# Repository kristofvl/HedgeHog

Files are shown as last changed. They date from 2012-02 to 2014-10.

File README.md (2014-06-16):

More information about this package can currently be found at:
 http://kristofvl.github.io/HedgeHog/ 

****************************************************************

In short, this repository contains three packages:

1. The HedgeHog firmware (operating system), requires:
    - MPLAB X (free IDE, download from Microchip.com)
    - Microchip Application Library (free library set, download 
      from Microchip.com)

2. The HedgeHog Graphical interface software, requires:
    - the basic python libraries
    - matplotlib

3. The hardware design files for the HedgeHog sensor, requires:
    - eagleCAD (free PCB design tool, download from 
      CadSoftusa.com)

****************************************************************

# User Manual

This manual will help you use your HedgeHog properly. Therefore, we will discuss the following themes

[1) Prepare your computer](#prepare-your-computer)<br>
[2) Configure the HedgeHog](#configure-the-hedgehog)<br>
[3) Start logging](#start-logging)<br>
[4) Download the logged data](#download-the-logged-data)<br>
[5) Display the downloaded data](#display-the-downloaded-data)<br>

## Prepare your computer

There is some software required on your computer in order for the graphical interface to work

* the basic python libraries (https://www.python.org/)
* matplotlib (http://matplotlib.org/)

Once this software is installed, please clone this repository by executing the command

	$ git clone https://github.com/kristofvl/HedgeHog

Now execute the installation script

	$ ./HedgeHog/HHG/install_HHG.py

This will create a few Desktop shortcuts to scripts, that will be discussed later on. Now your computer is set up for working with the HedgeHog.

## Configure the HedgeHog

If you plug in the HedgeHog into the USB-Connector of your PC, it should be recognized correctly now. The install command has created a shortcut to the configuration script. Start the script and choose the desired configuration, then click *Save Settings*. The HedgeHog will unmount, apply the settings and then mount again by itself. Do not unplug it during this process! 
In the configuration script you also have the option of formating your SD-Card. By pressing format the HedgeHog will unmount, format the SD-Card and then remount again.
An other way of formatting your HedgeHog is by using the dd command. In this example, the HedgeHog is mounted at /dev/sdb.

	- cd ~/HedgeHog/HHG/
	- dd if=dd_img/dd.img of=/dev/sdb; sync

Don't forget to configure the HedgeHog after formatting.

In case you dont want to start the configuration script using the created buttons, you can also run them in a terminal. The script is in the folder *~/HedgeHog/HHG/* and is named *conf_HHG.py*. To run it, go to the folder and execute

	- python conf_HHG.py /media/<username>/HedgeHog<HHG-device_id>/config.URE

## Start logging

Now that your HedgeHog has the right configuration, you are ready to start logging. Use the start script, that was also created during the installation. You will find the shortcut on your Desktop. Choose the logging period. The default is set to one week. After pressing start, the HedgeHog will disconnect automatically and start logging. Remember to unplug it form the USB-Connector instantaneously after starting it.

Since firmware version 1.4000, the HedgeHog will continue logging as long as it has energy supply, even if it is plugged into the USB-Connector. When plugged in, the HedgeHog will interrupt the logging process and resume, as soon as it is plugged out. You can visualize the data, as shown in [4) Download the logged data](#download-the-logged-data) and [5) Display the downloaded data](#display-the-downloaded-data) when the device is attatched to your PC.

In case you dont want to start the script using the created buttons, you can also run them in a terminal. The script is in the folder *~/HedgeHog/HHG/* and is named *start_HHG.py*. To run it, go to the folder and execute

	- python start_HHG.py /media/<username>/HedgeHog<HHG-device_id>/config.URE

## Download the logged data

To download the logged data, you can use the download script. A shortcut to the script was also created during the installation. The data will be saved at 

	- ~/hhg_logs/<HHG_device_id>/<date>/d.npz 

where 'HHG-device_id' is the number you entered in the configuration interface and 'date' is the starting date.

## Display the downloaded data

To visualize the data, use the python script in the repository as follows:

	- cd ~/HedgeHog/HHG/
	- ./viz_HHG.py ~/hhg_logs/<HHG_device_id>/<date>/d.npz 

where 'HHG-device_id' is the number you entered in the configuration interface and 'date' is the starting date.

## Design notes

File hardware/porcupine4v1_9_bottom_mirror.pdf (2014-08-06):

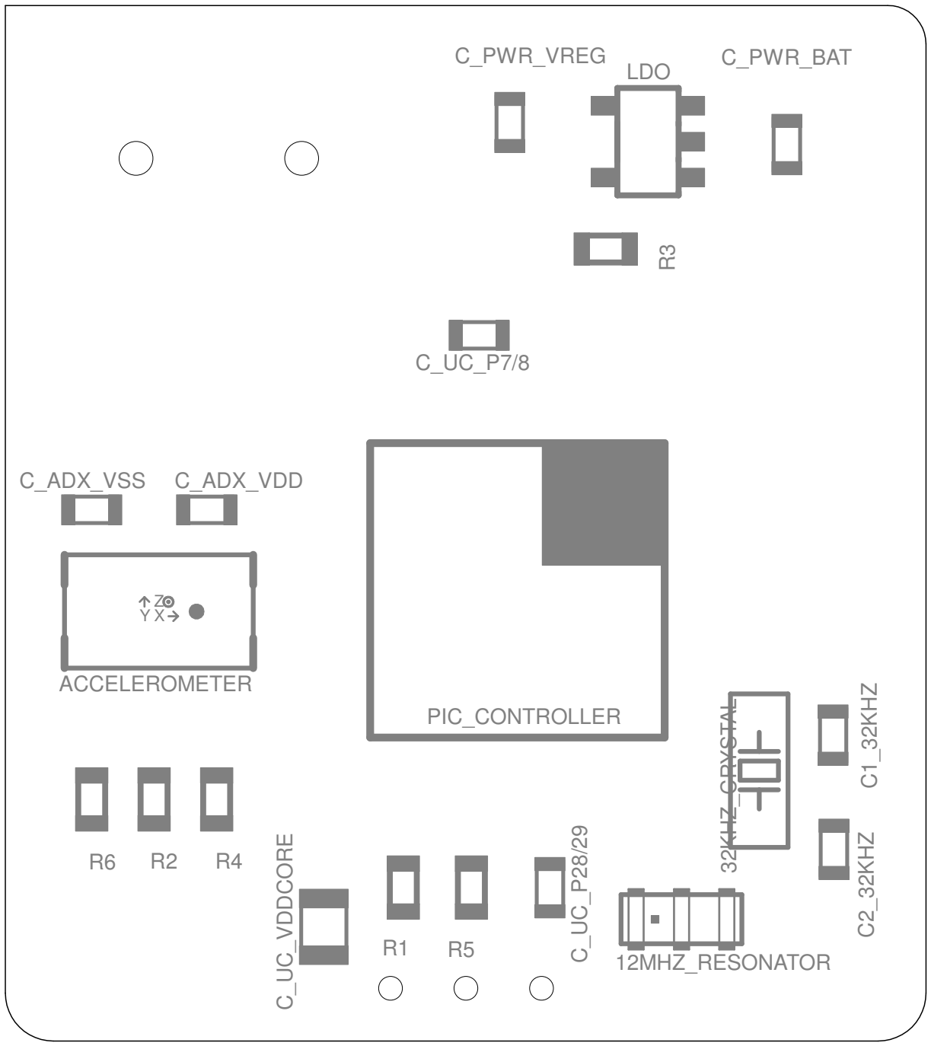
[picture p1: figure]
12MHZ_RESONATOR ³²KHZ_CRYSTAL; C_PWR_BAT; ACCELEROMETER; C_ADX_VSS; C_ADX_VDD; C_PWR_VREG; PIC_CONTROLLER; C2_32KHZ C1_32KHZ; C_UC_VDDCORE; LDO

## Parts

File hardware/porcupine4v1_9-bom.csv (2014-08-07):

BILL OF MATERIAL FROM TEST_WIDERSTAENDE_AUS_RCL.SCH, 29 PARTS, GROUPED BY VALUES, AS OF 05.10.2010 16:00:00
Part | Value | Device | Package | Description | Description2 | Qty | Place_YES/NO | Povided_by_customer_YES/NO | Distributor | Ordernumber | Weblink | Remarks_customer | Unit_price | Total_price | REMARKS_BETA | OPTION1 | OPTION2 | OPTION3
12MHZ_RESONATOR | RESONATORPRQC-C | RESONATORPRQC-C | PRQC-C |  |  | 1 | YES | NO | DigiKey | 478-6318-1-ND | http://www.digikey.de/product-detail/de/PRQC12.00CR5010X000/478-6318-1-ND/2506334 |  | 0.389
32KHZ_CRYSTAL | SMD_CRYSTAL | SMD_CRYSTAL | SMD_CRYSTAL |  |  | 1 | YES | NO | Farnell | 2101349 | de.farnell.com/2101349 |  | 0.801
ACCELEROMETER | ADXL345 | ADXL345 | LGA14 |  |  | 1 | YES | NO | Farnell | 1853935 | de.farnell.com/1853935 |  | 4.15
BAT | 53048-02 | 53048-02 | 53048-02 | CONNECTOR |  | 1 | YES | NO | Farnell | 1012259 | de.farnell.com/1012259 |  | 0.298
C1_32KHZ, C2_32KHZ | 22p | C-EUC0603K | C0603K | CAPACITOR, European symbol |  | 2 | YES | NO | Farnell | 1759057 | de.farnell.com/1759057 |  | 0.009
CHARGER | MAX1551 | MAX1551 | SOT23-5L | Dual-Input USB/AC Adapter 1-Cell Li+ Battery Chargers |  | 1 | YES | NO | Farnell | 1628221 | de.farnell.com/1628221 |  | 1.69
C_ADX_VDD, C_UC_P37 | 0.1u | C-EUC0603K | C0603K | CAPACITOR, European symbol |  | 2 | YES | NO | Farnell | 1759016 | de.farnell.com/1759016 |  | 0.007
C_ADX_VSS, C_PWR_VREG, C_PWR_VUSB | 1u | C-EUC0603K | C0603K | CAPACITOR, European symbol |  | 3 | YES | NO | Farnell | 1759399 | de.farnell.com/1759399 |  | 0.009
C_PWR_BAT | 4.7u | C-EUC0603K | C0603K | CAPACITOR, European symbol |  | 1 | YES | NO | Farnell | 2362098 | de.farnell.com/2362098 |  | 0.053
C_UC_P7/8, C_UC_P28/29 | 0.22u | C-EUC0603K | C0603K | CAPACITOR, European symbol |  | 2 | YES | NO | Farnell | 1759403 | de.farnell.com/1759403 |  | 0.021
C_UC_VDDCORE | 10u | C-EUC0805K | C0805K | CAPACITOR, European symbol | Capacitor, 0805, 10uF, 16V | 1 | YES | NO | Farnell | 1759136 | de.farnell.com/1759136 |  | 0.046
LDO | MCP1824 | MCP1824 | SOT-23-5 | MCP1824T-3302E/OT |  | 1 | YES | NO | Farnell | 1578387 | de.farnell.com/1578387 |  | 0.322
LIGHTSENSE | TSL250 | TSL250 | TSL |  |  | 1 | NO | NO
PIC_CONTROLLER | PIC_P2V6 | PIC_P2V6 | QFN44ML8X8 |  |  | 1 | YES | NO | Farnell | 1706311 | de.farnell.com/1706311 | 10 in EU / 67 in GB | 2.72
R1, R2, R3, R4, R5, R6 | 10k | R-EU_R0603 | R0603 | RESISTOR, European symbol | RESISTOR, 0.1W, 1% | 6 | YES | NO | Farnell | 1469749 | de.farnell.com/1469749 |  | 0.018
SDCARD_CON | MICROSD_CONN | MICROSD_CONN | 460DA40013 |  |  | 1 | YES | NO | Farnell | 1686452 | de.farnell.com/1686452 |  | 1.83
USB_CON | USBCON | USBCON | 248601 | MINI USB 2.0 Connector TypeB |  | 1 | YES | NO | Farnell | 2112367 | de.farnell.com/2112367 |  | 0.41
X1 | PROGCON | PROGCON | 53047-05-OCT | Programmer Connector |  | 1 | NO | NO

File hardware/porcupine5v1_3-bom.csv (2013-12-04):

Part | Value | Device | Package | Description | Description2 | Qty | Place_YES/NO | Povided_by_customer_YES/NO | Distributor | Ordernumber | Weblink | Remarks_customer | Unit_price | Total_price | REMARKS_BETA | OPTION1 | OPTION2 | OPTION3
ACCERELOMETER | ADXL345 | ADXL345 | LGA14 |  |  | 1 | YES | NO | Farnell | 1853935 | de.farnell.com/1853935
BAT | 53048-02 | 53048-02 | 53048-02 | CONNECTOR |  | 1 | YES | NO | Farnell | 1012259 | de.farnell.com/1012259
C1_32KHZ, C2_32KHZ | 22p | C-EUC0603K | C0603K | CAPACITOR, European symbol |  | 2 | YES | NO | Farnell | 1759057 | de.farnell.com/1759057
CHARGER | MAX1551 | MAX1551 | SOT23-5L | Dual-Input USB/AC Adapter 1-Cell Li+ Battery Chargers |  | 1 | YES | NO | Farnell | 1628221 | de.farnell.com/1628221
CON_OLED | OLED_DENSITRON | OLED_DENSITRON | CON_DD-12864WE-1A |  |  | 1 | NO | NO | Farnell | 1829709 | de.farnell.com/1829709
C_ADX_VDD, C_UC_P37 | 0.1u | C-EUC0603K | C0603K | CAPACITOR, European symbol |  | 2 | YES | NO | Farnell | 1759016 | de.farnell.com/1759016
C_ADX_VSS, C_OL_VBREF, C_OL_VDD2, C_PWR_BAT, C_PWR_VREG, C_PWR_VUSB | 1u | C-EUC0603K | C0603K | CAPACITOR, European symbol |  | 6 | YES | NO | Farnell | 1759407 | de.farnell.com/1759407
C_OL_APP_VDD | 10u low ESR | CPOL-EUA/3216-18R | A/3216-18R | POLARIZED CAPACITOR, European symbol |  | 1 | YES | NO | Farnell | 1432318 | de.farnell.com/1432318 | CHECK ESR
C_OL_FB | 1n | C-EUC0603K | C0603K | CAPACITOR, European symbol | Kondensator, 1nF, 50V, 0603, SMD | 1 | YES | NO | Farnell | 722170 | de.farnell.com/722170
C_OL_VCOMH | 4.7u | C-EUC0603K | C0603K | CAPACITOR, European symbol |  | 1 | YES | NO | Farnell | 1833803 | de.farnell.com/1833803
C_OL_VPP | 6.8u low ESR | CPOL-EUA/3216-18R | A/3216-18R | POLARIZED CAPACITOR, European symbol |  | 1 | YES | NO | Farnell | 1457431 | de.farnell.com/1457431 | CHECK ESR
C_PWR_SW, C_UC_VDDCORE | 10u | C-EUC0805K | C0805K | CAPACITOR, European symbol | Capacitor, 0805, 10uF, 16V | 2 | YES | NO | Farnell | 1288204 | de.farnell.com/1288204
C_UC_P7/8, C_UC_P28/29 | 0.22u | C-EUC0603K | C0603K | CAPACITOR, European symbol |  | 2 | YES | NO | Farnell | 1759403 | de.farnell.com/1759403
DIOD_OL | MBR0520 | MBR0520 | SOD123 |  |  | 1 | YES | NO | Farnell | 1467521 | de.farnell.com/1467521
LDO | MCP1824 | MCP1824 | SOT-23-5 | MCP1824T-3302E/OT |  | 1 | YES | NO | Farnell | 1578387 | de.farnell.com/1578387
LIGHTSENSE | TSL250 | TSL250 | TSL |  |  | 1 | NO | NO | Farnell | 1182346 | de.farnell.com/1182346
L_OL | 10uH | LQH3NP | 1212_FOR_INDUCTANCE |  |  | 1 | YES | NO | Farnell | 2219251 | de.farnell.com/2219251
N_MOS_OL |  | MGSF1N02LT1 | SOT-23 | MOS FET |  | 1 | YES | NO | Farnell | 9845372 | de.farnell.com/9845372
PIC_CONTROLLER | PIC_P2V6 | PIC_P2V6 | QFN44ML8X8 |  |  | 1 | YES | NO | Farnell | 1706311 | de.farnell.com/1706311
R1, R2, R3, R4, R5, R6, R7 | 10k | R-EU_R0603 | R0603 | RESISTOR, European symbol | RESISTOR, 0.1W, 1% | 7 | YES | NO | Farnell | 1469748 | de.farnell.com/1469748
R8 | 0.12 1% 0.5W | RESISTOR_PAN_ERJB3CFR12V | 0805_UPSIDEDOWN |  |  | 1 | YES | NO | Farnell | 1750969 | de.farnell.com/1750969
R9 | 110k 1% 0.125W | R-EU_R0603 | R0603 | RESISTOR, European symbol | RESISTOR, 0603, 110K, 1% | 1 | YES | NO | Farnell | 2138501 | de.farnell.com/2138501
R10 | 820k | R-EU_R0603 | R0603 | RESISTOR, European symbol | RESISTOR, 0.1W, 1% | 1 | YES | NO | Farnell | 2138597 | de.farnell.com/2138597
R11, R12 | 930k 1% | R-EU_R0603 | R0603 | RESISTOR, European symbol | RESISTOR, 0603, 931K, 1% | 2 | YES | NO | Farnell | 2138604 | de.farnell.com/2138604
RESONATOR | RESONATORPRQC-S | RESONATORPRQC-S | PRQC | Ceramic Resonator with caps |  | 1 | YES | NO | DigiKey | 478-6318-1-ND | http://www.digikey.de/product-detail/de/PRQC12.00CR5010X000/478-6318-1-ND/2506334
SDCARD_CON | MICROSD_CONN | MICROSD_CONN | 460DA40013 |  |  | 1 | YES | NO | Farnell | 1686452 | de.farnell.com/1686452
SMD_CRYSTAL | SMD_CRYSTAL | SMD_CRYSTAL | SMD_CRYSTAL |  |  | 1 | YES | NO | Farnell | 2101349 | de.farnell.com/2101349
USB_CON | USBCON | USBCON | 248601 | MINI USB 2.0 Connector TypeB |  | 1 | YES | NO | Farnell | 2112367 | de.farnell.com/2112367
X1 | PROGCON | PROGCON | 53047-05-OCT | Programmer Connector |  | 1 | NO

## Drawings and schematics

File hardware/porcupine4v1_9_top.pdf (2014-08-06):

## BAT

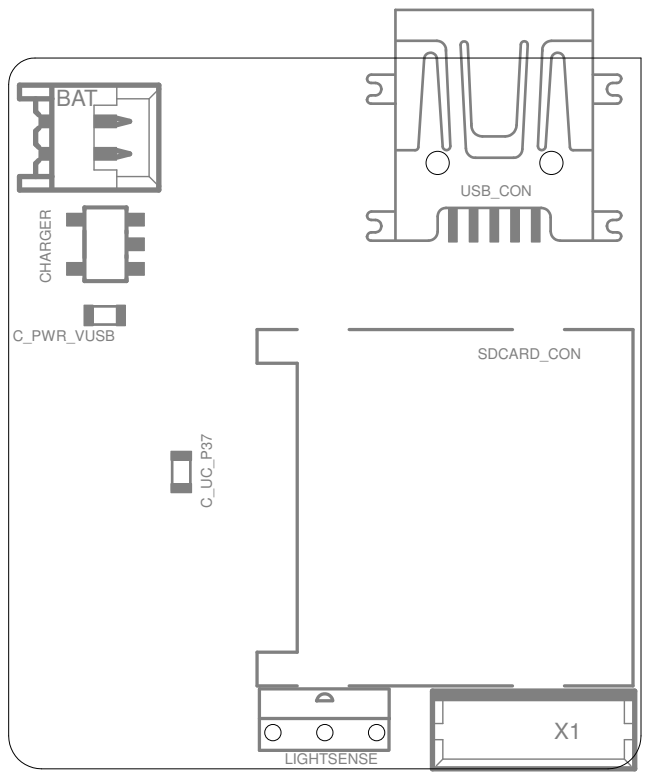
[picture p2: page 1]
LIGHTSENSE; SDCARD_CON; USB_CON; C_PWR_VUSB CHARGER

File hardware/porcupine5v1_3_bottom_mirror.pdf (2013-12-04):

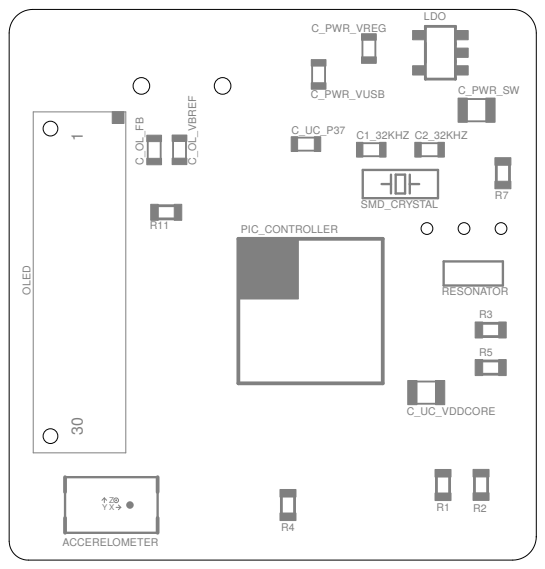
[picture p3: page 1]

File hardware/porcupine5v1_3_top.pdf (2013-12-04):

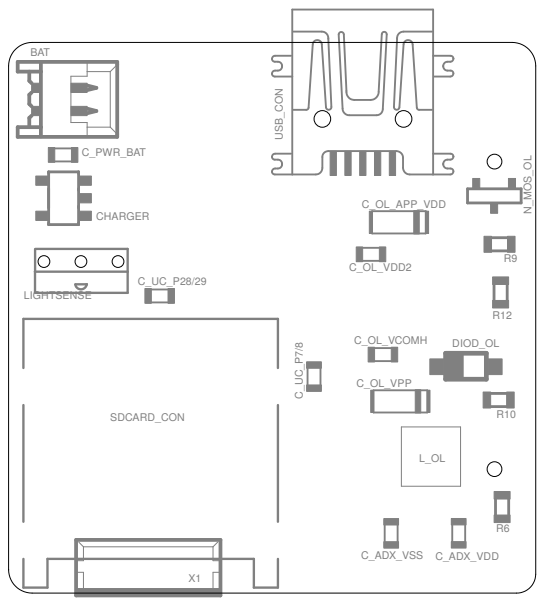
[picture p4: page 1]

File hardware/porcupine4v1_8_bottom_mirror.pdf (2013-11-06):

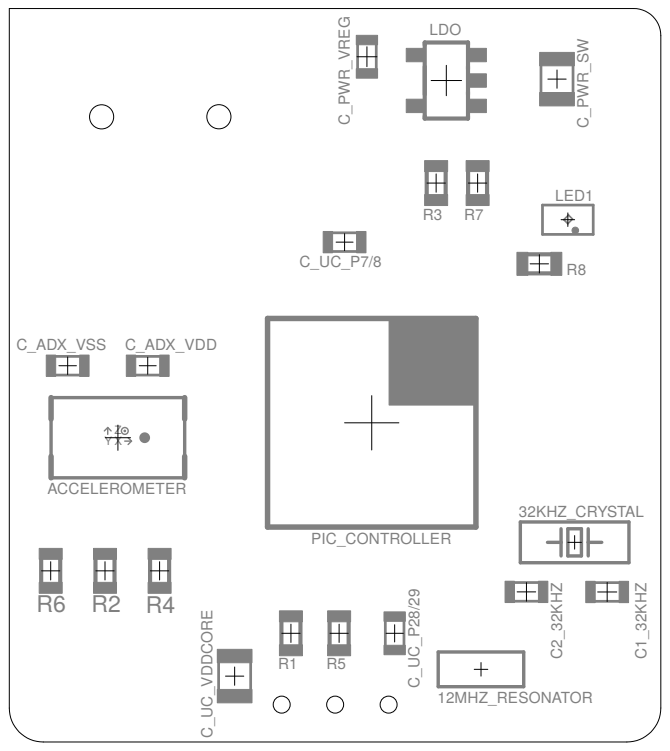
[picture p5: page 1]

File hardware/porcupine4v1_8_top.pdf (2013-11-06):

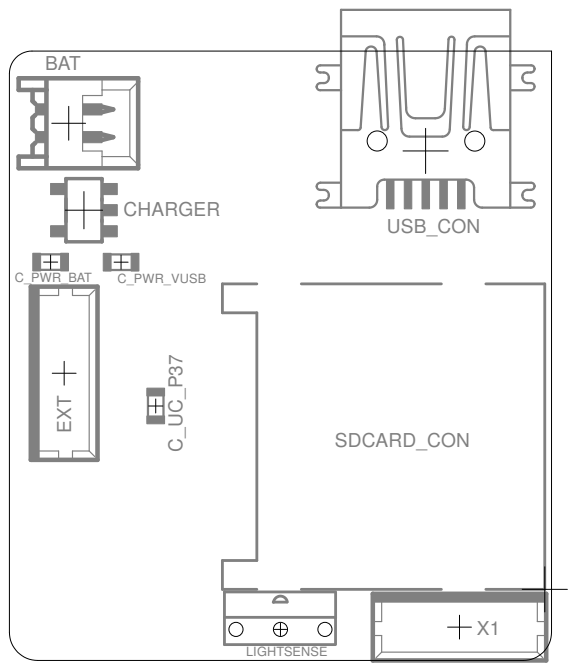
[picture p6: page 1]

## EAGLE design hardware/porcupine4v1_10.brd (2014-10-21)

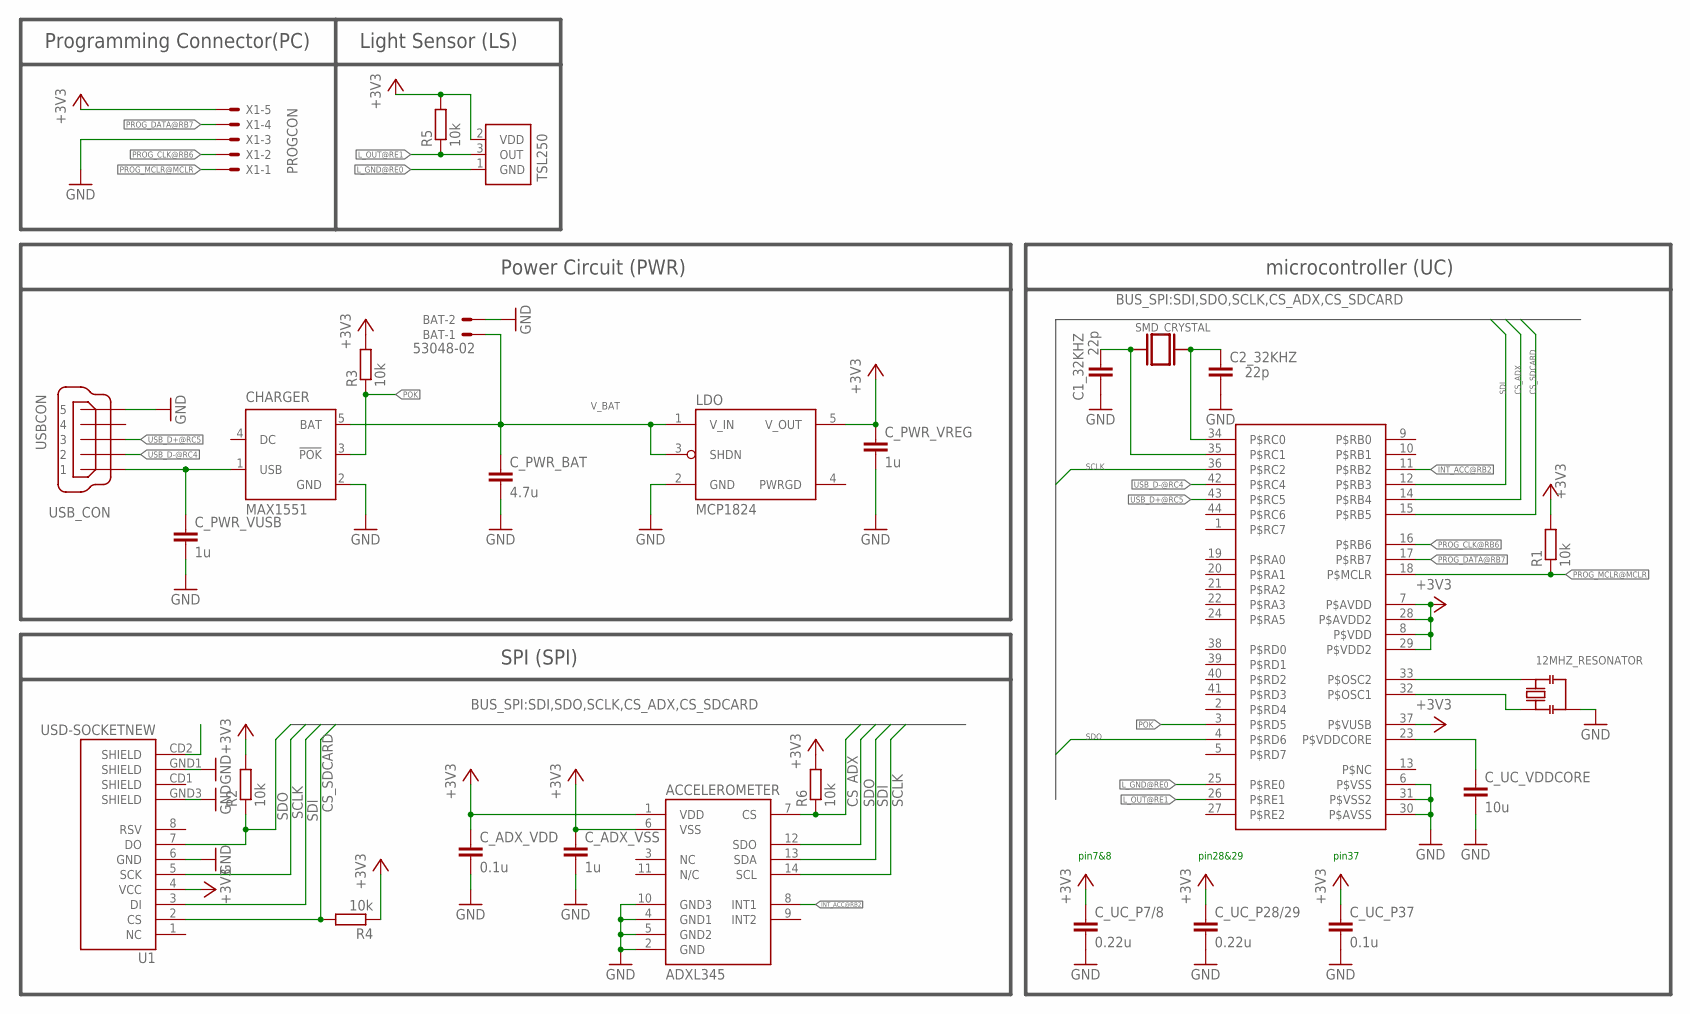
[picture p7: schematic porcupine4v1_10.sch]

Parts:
12MHZ_RESONATOR: RESONATORPRQC-C; PRQC-C
32KHZ_CRYSTAL: SMD_CRYSTAL
ACCELEROMETER: ADXL345; LGA14
BAT: 53048-02
C1_32KHZ, C2_32KHZ: 22p; C0603K
CHARGER: MAX1551; SOT23-5L
C_ADX_VDD: 0.1u; C0603K
C_ADX_VSS: 1u; C0603K
C_PWR_BAT: 4.7u; C0603K
C_PWR_VREG: 1u; C0603K
C_PWR_VUSB: 1u; C0603K
C_UC_P7/8, C_UC_P28/29: 0.22u; C0603K
C_UC_P37: 0.1u; C0603K
C_UC_VDDCORE: 10u; C0805K
LDO: MCP1824; SOT-23-5
LIGHTSENSE: TSL250; TSL
PIC_CONTROLLER: PIC_P2V6; QFN44ML8X8
R1, R2, R3, R4, R5, R6: 10k; R0603
U1: USD-SOCKETNEW; MICRO-SD-SOCKET-PP
USB_CON: USBCON; 248601
X1: PROGCON; 53047-05-OCT

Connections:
+3V3: ACCELEROMETER.1 (VDD), ACCELEROMETER.6 (VSS), C_ADX_VDD.1, C_ADX_VSS.1, C_PWR_VREG.1, C_UC_P7/8.1, C_UC_P28/29.1, C_UC_P37.1, LDO.5 (V_OUT), LIGHTSENSE.2 (VDD), PIC_CONTROLLER.7 (P$AVDD), PIC_CONTROLLER.8 (P$VDD), PIC_CONTROLLER.28 (P$AVDD2), PIC_CONTROLLER.29 (P$VDD2), PIC_CONTROLLER.37 (P$VUSB), R1.2, R2.2, R3.2, R4.1, R5.2, R6.2, U1.4 (VCC), X1.5
CS_ADX: ACCELEROMETER.7 (CS), PIC_CONTROLLER.14 (P$RB4), R6.1
CS_SDCARD: PIC_CONTROLLER.15 (P$RB5), R4.2, U1.2 (CS)
GND: 12MHZ_RESONATOR.2_GND (GND), ACCELEROMETER.2 (GND), ACCELEROMETER.4 (GND1), ACCELEROMETER.5 (GND2), ACCELEROMETER.10 (GND3), BAT.2, C1_32KHZ.2, C2_32KHZ.2, CHARGER.2 (GND), C_ADX_VDD.2, C_ADX_VSS.2, C_PWR_BAT.2, C_PWR_VREG.2, C_PWR_VUSB.2, C_UC_P7/8.2, C_UC_P28/29.2, C_UC_P37.2, C_UC_VDDCORE.2, LDO.2 (GND), PIC_CONTROLLER.6 (P$VSS), PIC_CONTROLLER.30 (P$AVSS), PIC_CONTROLLER.31 (P$VSS2), U1.6 (GND), U1.GND1 (SHIELD), U1.GND3 (SHIELD), USB_CON.5, X1.3
INT_ACC@RB2: ACCELEROMETER.8 (INT1), PIC_CONTROLLER.11 (P$RB2)
L_GND@RE0: LIGHTSENSE.1 (GND), PIC_CONTROLLER.25 (P$RE0)
L_OUT@RE1: LIGHTSENSE.3 (OUT), PIC_CONTROLLER.26 (P$RE1), R5.1
unnamed: 12MHZ_RESONATOR.3 (2), PIC_CONTROLLER.32 (P$OSC1)
unnamed: 12MHZ_RESONATOR.1, PIC_CONTROLLER.33 (P$OSC2)
unnamed: 32KHZ_CRYSTAL.P$2 (2), C2_32KHZ.1, PIC_CONTROLLER.34 (P$RC0)
unnamed: 32KHZ_CRYSTAL.P$1 (1), C1_32KHZ.1, PIC_CONTROLLER.35 (P$RC1)
P$RD7: PIC_CONTROLLER.5 (P$RD7)
POK: CHARGER.3 (!POK), PIC_CONTROLLER.3 (P$RD5), R3.1
PROG_CLK@RB6: PIC_CONTROLLER.16 (P$RB6), X1.2
PROG_DATA@RB7: PIC_CONTROLLER.17 (P$RB7), X1.4
PROG_MCLR@MCLR: PIC_CONTROLLER.18 (P$MCLR), R1.1, X1.1
SCLK: ACCELEROMETER.14 (SCL), PIC_CONTROLLER.36 (P$RC2), U1.5 (SCK)
SDI: ACCELEROMETER.13 (SDA), PIC_CONTROLLER.12 (P$RB3), U1.3 (DI)
SDO: ACCELEROMETER.12 (SDO), PIC_CONTROLLER.4 (P$RD6), R2.1, U1.7 (DO)
USB_D+@RC5: PIC_CONTROLLER.43 (P$RC5), USB_CON.3
USB_D-@RC4: PIC_CONTROLLER.42 (P$RC4), USB_CON.2
VDDCORE: C_UC_VDDCORE.1, PIC_CONTROLLER.23 (P$VDDCORE)
V_BAT: BAT.1, CHARGER.5 (BAT), C_PWR_BAT.1, LDO.1 (V_IN), LDO.3 (SHDN)
V_USB: CHARGER.1 (USB), C_PWR_VUSB.1, USB_CON.1

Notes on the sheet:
Programming Connector(PC)
pin28&29
pin37
Power Circuit (PWR)
SPI (SPI)
microcontroller (UC)
Light Sensor (LS)
pin7&8

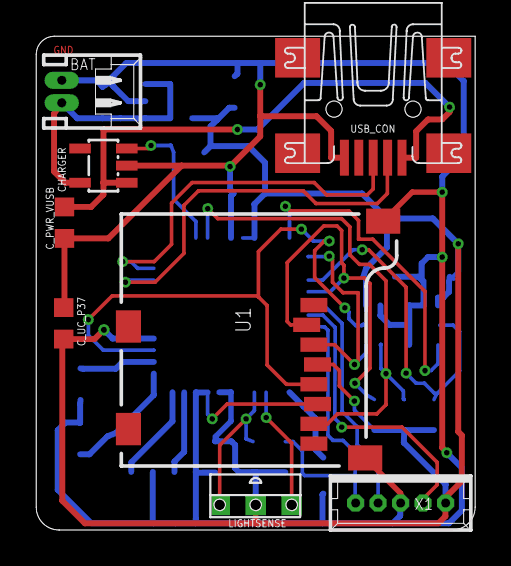
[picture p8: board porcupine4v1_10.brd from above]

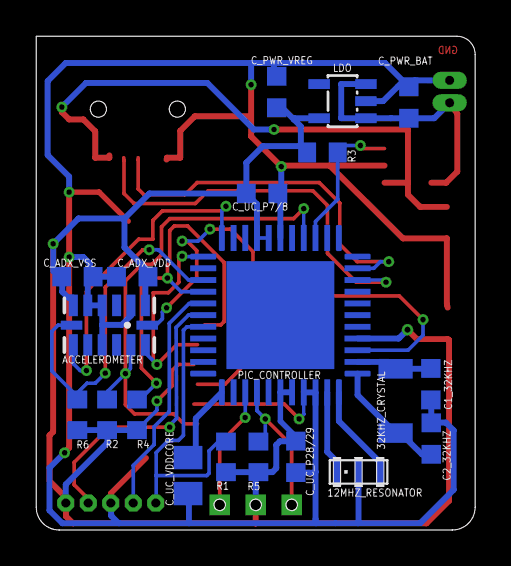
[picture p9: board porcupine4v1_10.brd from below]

Board: 2 copper layers, 24.4 x 27.4 mm, 28 parts (20 on the bottom side), 23 nets.

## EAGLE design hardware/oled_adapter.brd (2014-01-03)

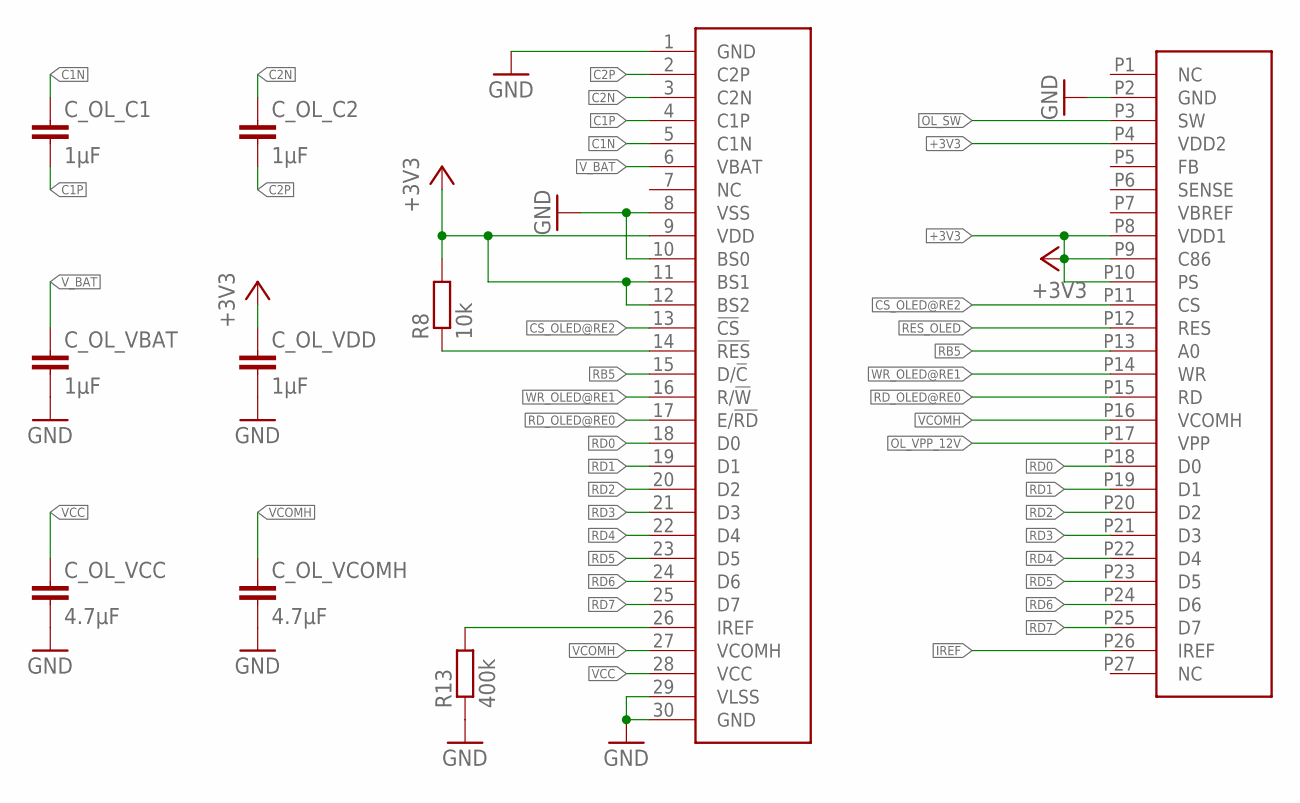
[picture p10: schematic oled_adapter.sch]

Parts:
CON_OLED: OLED_DENSITRON; CON_DD-12864WE-1A
C_OL_C1, C_OL_C2: 1µF; C0603K
C_OL_VBAT: 1µF; C0603K
C_OL_VCC: 4.7µF; C0603K
C_OL_VCOMH: 4.7µF; C0603K
C_OL_VDD: 1µF; C0603K
OLED: DD-12864WE-4A; CON_DD-12864WE-4A
R8: 10k; R0603
R13: 400k; R0603

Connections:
+3V3: CON_OLED.P4 (VDD2), CON_OLED.P8 (VDD1), CON_OLED.P9 (C86), CON_OLED.P10 (PS), C_OL_VDD.1, OLED.9 (VDD), OLED.11 (BS1), OLED.12 (BS2), R8.2
C1N: C_OL_C1.1, OLED.5 (C1N)
C1P: C_OL_C1.2, OLED.4 (C1P)
C2N: C_OL_C2.1, OLED.3 (C2N)
C2P: C_OL_C2.2, OLED.2 (C2P)
CS_OLED@RE2: CON_OLED.P11 (CS), OLED.13 (!CS)
GND: CON_OLED.P2 (GND), C_OL_VBAT.2, C_OL_VCC.2, C_OL_VCOMH.2, C_OL_VDD.2, OLED.1 (GND), OLED.8 (VSS), OLED.10 (BS0), OLED.29 (VLSS), OLED.30 (GND), R13.1
IREF: CON_OLED.P26 (IREF), OLED.26 (IREF), R13.2
OL_SW: CON_OLED.P3 (SW)
OL_VPP_12V: CON_OLED.P17 (VPP)
RB5: CON_OLED.P13 (A0), OLED.15 (D/!C)
RD0: CON_OLED.P18 (D0), OLED.18 (D0)
RD1: CON_OLED.P19 (D1), OLED.19 (D1)
RD2: CON_OLED.P20 (D2), OLED.20 (D2)
RD3: CON_OLED.P21 (D3), OLED.21 (D3)
RD4: CON_OLED.P22 (D4), OLED.22 (D4)
RD5: CON_OLED.P23 (D5), OLED.23 (D5)
RD6: CON_OLED.P24 (D6), OLED.24 (D6)
RD7: CON_OLED.P25 (D7), OLED.25 (D7)
RD_OLED@RE0: CON_OLED.P15 (RD), OLED.17 (E/!RD)
RES_OLED: CON_OLED.P12 (RES), OLED.14 (!RES), R8.1
VCC: C_OL_VCC.1, OLED.28 (VCC)
VCOMH: CON_OLED.P16 (VCOMH), C_OL_VCOMH.1, OLED.27 (VCOMH)
V_BAT: C_OL_VBAT.1, OLED.6 (VBAT)
WR_OLED@RE1: CON_OLED.P14 (WR), OLED.16 (R/!W)

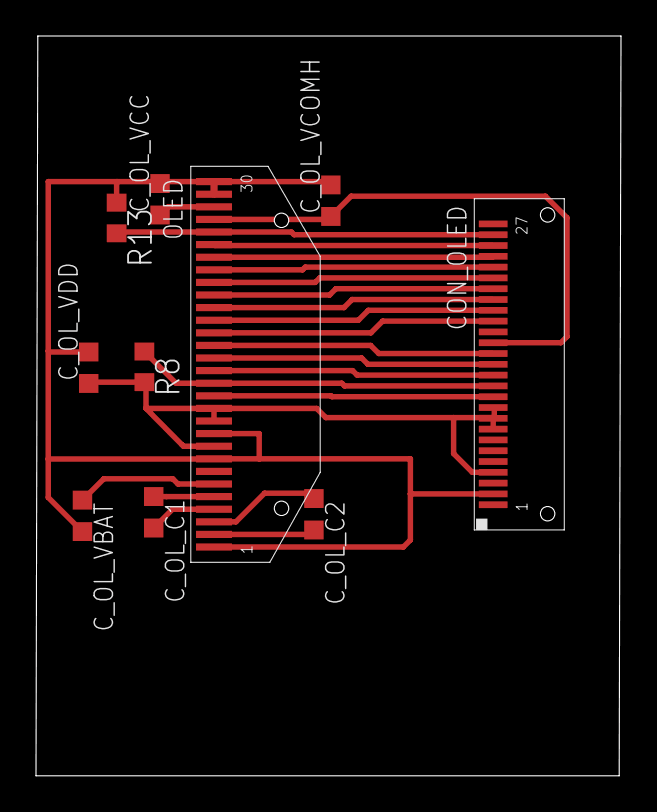
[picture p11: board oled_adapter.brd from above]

Board: 2 copper layers, 32.5 x 41.1 mm, 10 parts (0 on the bottom side), 23 nets.

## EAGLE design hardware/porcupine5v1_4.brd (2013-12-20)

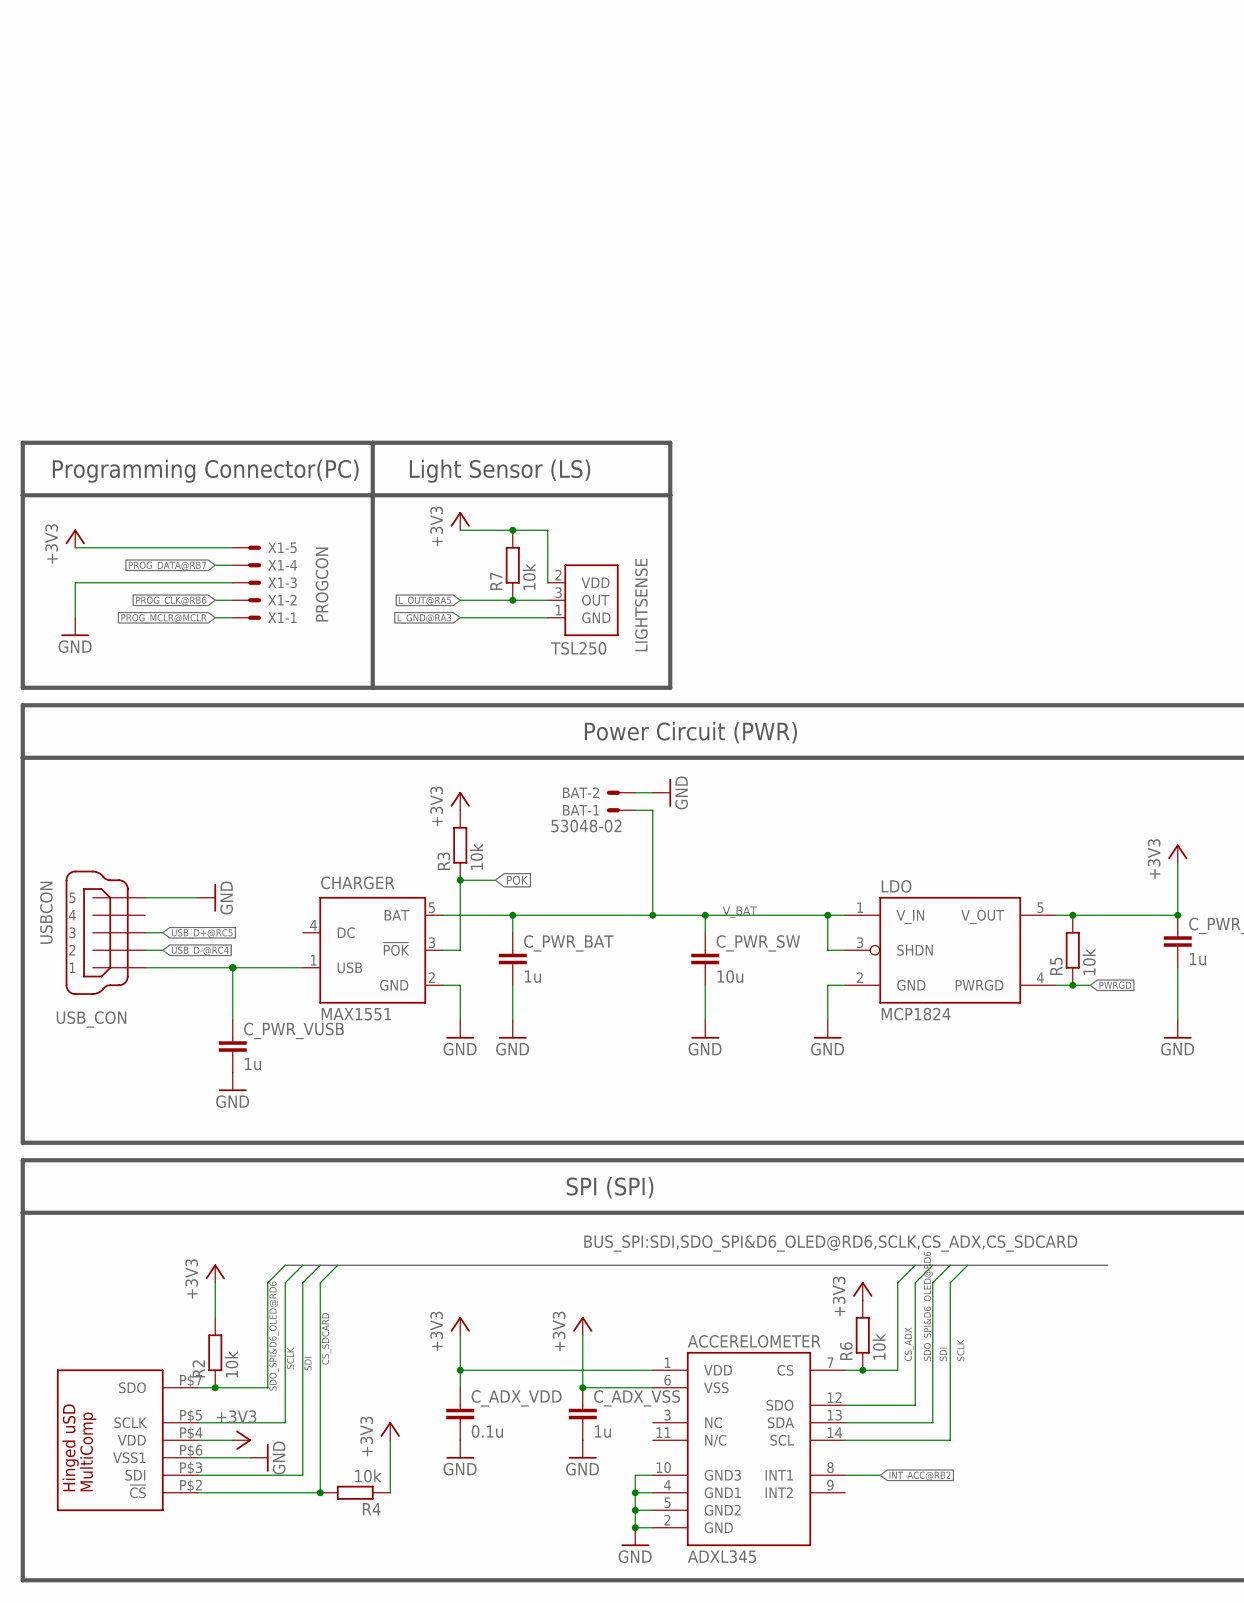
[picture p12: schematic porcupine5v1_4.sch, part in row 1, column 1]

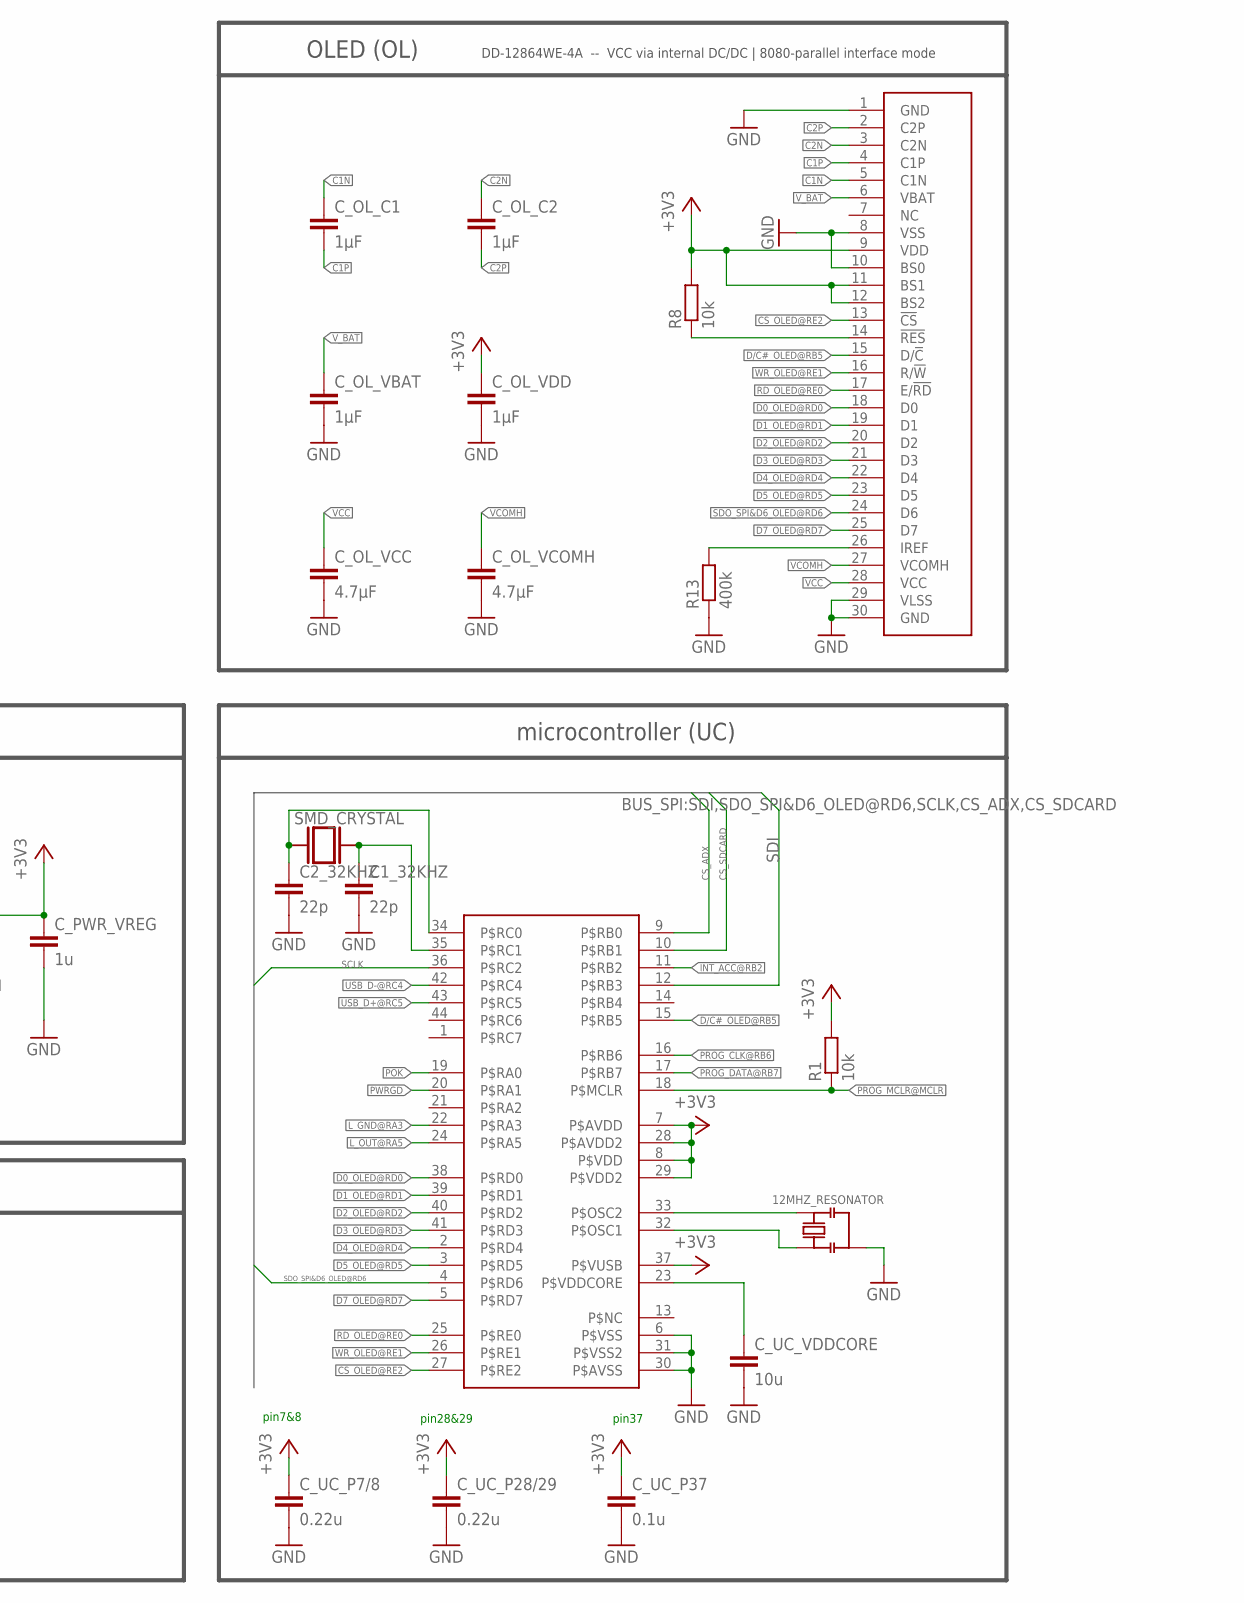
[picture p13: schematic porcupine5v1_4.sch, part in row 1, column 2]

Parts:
12MHZ_RESONATOR: RESONATORPRQC-C; PRQC-C
ACCERELOMETER: ADXL345; LGA14
BAT: 53048-02
C1_32KHZ, C2_32KHZ: 22p; C0603K
CHARGER: MAX1551; SOT23-5L
C_ADX_VDD: 0.1u; C0603K
C_ADX_VSS: 1u; C0603K
C_OL_C1, C_OL_C2: 1µF; C0603K
C_OL_VBAT: 1µF; C0603K
C_OL_VCC: 4.7µF; C0603K
C_OL_VCOMH: 4.7µF; C0603K
C_OL_VDD: 1µF; C0603K
C_PWR_BAT: 1u; C0603K
C_PWR_SW: 10u; C0805K
C_PWR_VREG: 1u; C0603K
C_PWR_VUSB: 1u; C0603K
C_UC_P7/8, C_UC_P28/29: 0.22u; C0603K
C_UC_P37: 0.1u; C0603K
C_UC_VDDCORE: 10u; C0805K
LDO: MCP1824; SOT-23-5
LIGHTSENSE: TSL250; TSL
OLED: DD-12864WE-4A; CON_DD-12864WE-4A
PIC_CONTROLLER: PIC_P2V6; QFN44ML8X8
R1, R2, R3, R4, R5, R6, R7, R8: 10k; R0603
R13: 400k; R0603
SDCARD_CON: MICROSD_CONN; 460DA40013
SMD_CRYSTAL: SMD_CRYSTAL
USB_CON: USBCON; 248601
X1: PROGCON; 53047-05-OCT

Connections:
+3V3: ACCERELOMETER.1 (VDD), ACCERELOMETER.6 (VSS), C_ADX_VDD.1, C_ADX_VSS.1, C_OL_VDD.1, C_PWR_VREG.1, C_UC_P7/8.1, C_UC_P28/29.1, C_UC_P37.1, LDO.5 (V_OUT), LIGHTSENSE.2 (VDD), OLED.9 (VDD), OLED.11 (BS1), OLED.12 (BS2), PIC_CONTROLLER.7 (P$AVDD), PIC_CONTROLLER.8 (P$VDD), PIC_CONTROLLER.28 (P$AVDD2), PIC_CONTROLLER.29 (P$VDD2), PIC_CONTROLLER.37 (P$VUSB), R1.2, R2.2, R3.2, R4.1, R5.2, R6.2, R7.2, R8.2, SDCARD_CON.P$4 (VDD), X1.5
C1N: C_OL_C1.1, OLED.5 (C1N)
C1P: C_OL_C1.2, OLED.4 (C1P)
C2N: C_OL_C2.1, OLED.3 (C2N)
C2P: C_OL_C2.2, OLED.2 (C2P)
CS_ADX: ACCERELOMETER.7 (CS), PIC_CONTROLLER.9 (P$RB0), R6.1
CS_OLED@RE2: OLED.13 (!CS), PIC_CONTROLLER.27 (P$RE2)
CS_SDCARD: PIC_CONTROLLER.10 (P$RB1), R4.2, SDCARD_CON.P$2 (!CS)
D0_OLED@RD0: OLED.18 (D0), PIC_CONTROLLER.38 (P$RD0)
D1_OLED@RD1: OLED.19 (D1), PIC_CONTROLLER.39 (P$RD1)
D2_OLED@RD2: OLED.20 (D2), PIC_CONTROLLER.40 (P$RD2)
D3_OLED@RD3: OLED.21 (D3), PIC_CONTROLLER.41 (P$RD3)
D4_OLED@RD4: OLED.22 (D4), PIC_CONTROLLER.2 (P$RD4)
D5_OLED@RD5: OLED.23 (D5), PIC_CONTROLLER.3 (P$RD5)
D7_OLED@RD7: OLED.25 (D7), PIC_CONTROLLER.5 (P$RD7)
D/C#_OLED@RB5: OLED.15 (D/!C), PIC_CONTROLLER.15 (P$RB5)
GND: 12MHZ_RESONATOR.2_GND (GND), ACCERELOMETER.2 (GND), ACCERELOMETER.4 (GND1), ACCERELOMETER.5 (GND2), ACCERELOMETER.10 (GND3), BAT.2, C1_32KHZ.2, C2_32KHZ.2, CHARGER.2 (GND), C_ADX_VDD.2, C_ADX_VSS.2, C_OL_VBAT.2, C_OL_VCC.2, C_OL_VCOMH.2, C_OL_VDD.2, C_PWR_BAT.2, C_PWR_SW.2, C_PWR_VREG.2, C_PWR_VUSB.2, C_UC_P7/8.2, C_UC_P28/29.2, C_UC_P37.2, C_UC_VDDCORE.2, LDO.2 (GND), OLED.1 (GND), OLED.8 (VSS), OLED.10 (BS0), OLED.29 (VLSS), OLED.30 (GND), PIC_CONTROLLER.6 (P$VSS), PIC_CONTROLLER.30 (P$AVSS), PIC_CONTROLLER.31 (P$VSS2), R13.1, SDCARD_CON.P$6 (VSS1), USB_CON.5, X1.3
INT_ACC@RB2: ACCERELOMETER.8 (INT1), PIC_CONTROLLER.11 (P$RB2)
IREF: OLED.26 (IREF), R13.2
L_GND@RA3: LIGHTSENSE.1 (GND), PIC_CONTROLLER.22 (P$RA3)
L_OUT@RA5: LIGHTSENSE.3 (OUT), PIC_CONTROLLER.24 (P$RA5), R7.1
unnamed: 12MHZ_RESONATOR.1, PIC_CONTROLLER.33 (P$OSC2)
unnamed: 12MHZ_RESONATOR.3 (2), PIC_CONTROLLER.32 (P$OSC1)
unnamed: C2_32KHZ.1, PIC_CONTROLLER.34 (P$RC0), SMD_CRYSTAL.P$1 (1)
unnamed: C1_32KHZ.1, PIC_CONTROLLER.35 (P$RC1), SMD_CRYSTAL.P$2 (2)
POK: CHARGER.3 (!POK), PIC_CONTROLLER.19 (P$RA0), R3.1
PROG_CLK@RB6: PIC_CONTROLLER.16 (P$RB6), X1.2
PROG_DATA@RB7: PIC_CONTROLLER.17 (P$RB7), X1.4
PROG_MCLR@MCLR: PIC_CONTROLLER.18 (P$MCLR), R1.1, X1.1
PWRGD: LDO.4 (PWRGD), PIC_CONTROLLER.20 (P$RA1), R5.1
RD_OLED@RE0: OLED.17 (E/!RD), PIC_CONTROLLER.25 (P$RE0)
RES_OLED: OLED.14 (!RES), R8.1
SCLK: ACCERELOMETER.14 (SCL), PIC_CONTROLLER.36 (P$RC2), SDCARD_CON.P$5 (SCLK)
SDI: ACCERELOMETER.13 (SDA), PIC_CONTROLLER.12 (P$RB3), SDCARD_CON.P$3 (SDI)
SDO_SPI&D6_OLED@RD6: ACCERELOMETER.12 (SDO), OLED.24 (D6), PIC_CONTROLLER.4 (P$RD6), R2.1, SDCARD_CON.P$7 (SDO)
USB_D+@RC5: PIC_CONTROLLER.43 (P$RC5), USB_CON.3
USB_D-@RC4: PIC_CONTROLLER.42 (P$RC4), USB_CON.2
VCC: C_OL_VCC.1, OLED.28 (VCC)
VCOMH: C_OL_VCOMH.1, OLED.27 (VCOMH)
VDDCORE: C_UC_VDDCORE.1, PIC_CONTROLLER.23 (P$VDDCORE)
VUSB: CHARGER.1 (USB), C_PWR_VUSB.1, USB_CON.1
V_BAT: BAT.1, CHARGER.5 (BAT), C_OL_VBAT.1, C_PWR_BAT.1, C_PWR_SW.1, LDO.1 (V_IN), LDO.3 (SHDN), OLED.6 (VBAT)
WR_OLED@RE1: OLED.16 (R/!W), PIC_CONTROLLER.26 (P$RE1)

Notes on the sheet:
Programming Connector(PC)
pin7&8
pin28&29
pin37
Power Circuit (PWR)
SPI (SPI)
OLED (OL)
microcontroller (UC)
Light Sensor (LS)
DD-12864WE-4A -- VCC via internal DC/DC | 8080-parallel interface mode

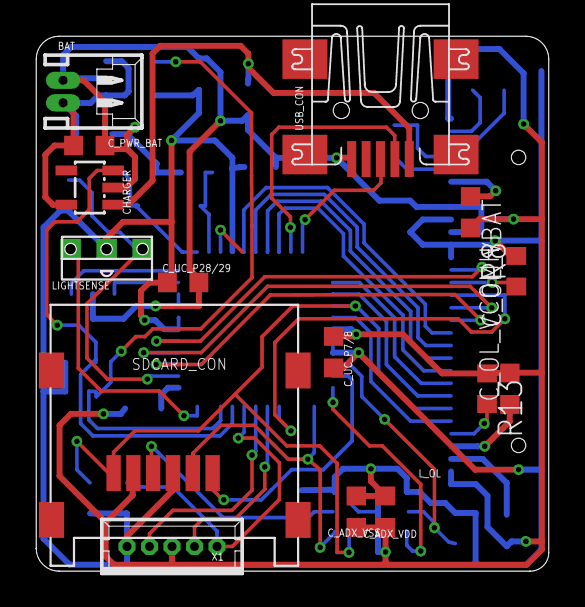
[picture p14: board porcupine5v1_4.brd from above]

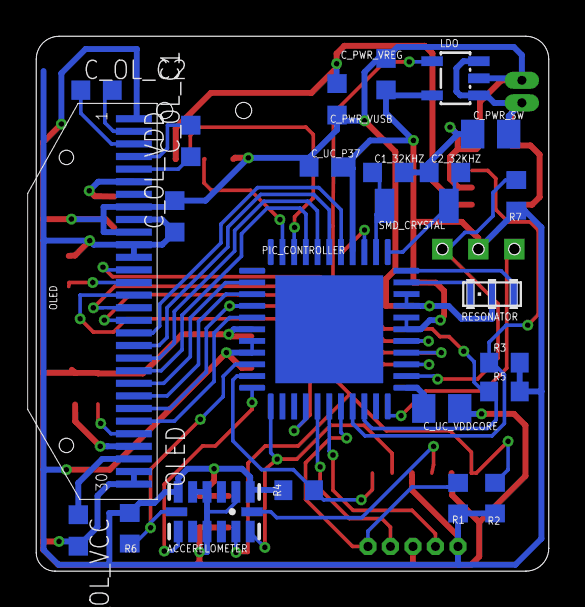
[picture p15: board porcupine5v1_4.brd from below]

Board: 2 copper layers, 28.5 x 29.7 mm, 39 parts (24 on the bottom side), 43 nets.

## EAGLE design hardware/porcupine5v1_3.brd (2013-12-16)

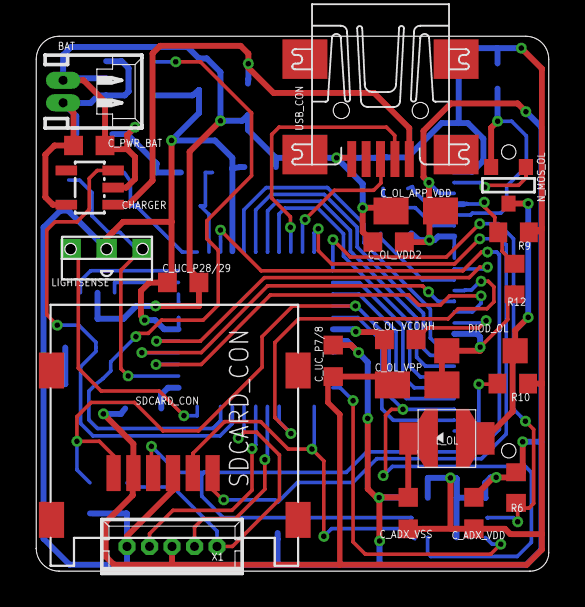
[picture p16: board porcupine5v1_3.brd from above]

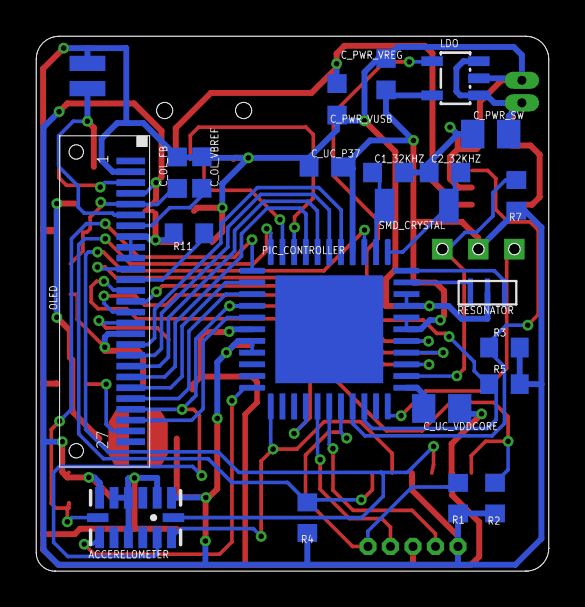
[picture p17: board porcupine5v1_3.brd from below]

Board: 2 copper layers, 28.5 x 29.7 mm, 45 parts (23 on the bottom side), 44 nets.

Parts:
ACCERELOMETER: ADXL345; LGA14
BAT: 53048-02
C1_32KHZ, C2_32KHZ: 22p; C0603K
CHARGER: MAX1551; SOT23-5L
CON_OLED: OLED_DENSITRON; CON_DD-12864WE-1A
C_ADX_VDD: 0.1u; C0603K
C_ADX_VSS: 1u; C0603K
C_OL_APP_VDD: 10µF/6.3V low ESR; A/3216-18R
C_OL_FB: 1n; C0603K
C_OL_VBREF: 1u; C0603K
C_OL_VCOMH: 4.7u; C0603K
C_OL_VDD2: 1µF/16V; C0603K
C_OL_VPP: 6.8µF/16V low ESR; A/3216-18R
C_PWR_BAT: 1u; C0603K
C_PWR_SW: 10u; C0805K
C_PWR_VREG: 1u; C0603K
C_PWR_VUSB: 1u; C0603K
C_UC_P7/8, C_UC_P28/29: 0.22u; C0603K
C_UC_P37: 0.1u; C0603K
C_UC_VDDCORE: 10u; C0805K
DIOD_OL: MBR0520; SOD123
LDO: MCP1824; SOT-23-5
LIGHTSENSE: TSL250; TSL
L_OL: 10µH; 1212_FOR_INDUCTANCE
N_MOS_OL: SOT-23
PIC_CONTROLLER: PIC_P2V6; QFN44ML8X8
R1, R2, R3, R4, R5, R6, R7: 10k; R0603
R8: 0.12 1% 0.5W; 0805_UPSIDEDOWN
R9: 110k 1%; R0603
R10: 820k; R0603
R11, R12: 930k 1%; R0603
RESONATOR: RESONATORPRQC-S; PRQC
SDCARD_CON: MICROSD_CONN; 460DA40013
SMD_CRYSTAL: SMD_CRYSTAL
USB_CON: USBCON; 248601
X1: PROGCON; 53047-05-OCT

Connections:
+3V3: ACCERELOMETER.1, ACCERELOMETER.6, CON_OLED.P4, CON_OLED.P8, CON_OLED.P9, CON_OLED.P10, C_ADX_VDD.1, C_ADX_VSS.1, C_OL_APP_VDD.+, C_OL_VDD2.2, C_PWR_VREG.1, C_UC_P7/8.1, C_UC_P28/29.1, C_UC_P37.1, LDO.5, LIGHTSENSE.2, L_OL.P$1, PIC_CONTROLLER.7, PIC_CONTROLLER.8, PIC_CONTROLLER.28, PIC_CONTROLLER.29, PIC_CONTROLLER.37, R1.2, R2.2, R3.2, R4.1, R5.2, R6.2, R7.2, R11.2, SDCARD_CON.P$4, X1.5
A0_OLED@RB5: CON_OLED.P13, PIC_CONTROLLER.15
CS_ADX: ACCERELOMETER.7, PIC_CONTROLLER.1, R6.1
CS_OLED@RE2: CON_OLED.P11, PIC_CONTROLLER.27
CS_SDCARD: PIC_CONTROLLER.44, R4.2, SDCARD_CON.P$2
D0_OLED@RD0: CON_OLED.P18, PIC_CONTROLLER.38
D1_OLED@RD1: CON_OLED.P19, PIC_CONTROLLER.39
D2_OLED@RD2: CON_OLED.P20, PIC_CONTROLLER.40
D3_OLED@RD3: CON_OLED.P21, PIC_CONTROLLER.41
D4_OLED@RD4: CON_OLED.P22, PIC_CONTROLLER.2
D5_OLED@RD5: CON_OLED.P23, PIC_CONTROLLER.3
D7_OLED@RD7: CON_OLED.P25, PIC_CONTROLLER.5
GND: ACCERELOMETER.2, ACCERELOMETER.4, ACCERELOMETER.5, ACCERELOMETER.10, BAT.2, C1_32KHZ.2, C2_32KHZ.2, CHARGER.2, CON_OLED.P2, C_ADX_VDD.2, C_ADX_VSS.2, C_OL_APP_VDD.-, C_OL_FB.2, C_OL_VBREF.2, C_OL_VCOMH.1, C_OL_VDD2.1, C_OL_VPP.-, C_PWR_BAT.2, C_PWR_SW.2, C_PWR_VREG.2, C_PWR_VUSB.2, C_UC_P7/8.2, C_UC_P28/29.2, C_UC_P37.2, C_UC_VDDCORE.2, LDO.2, PIC_CONTROLLER.6, PIC_CONTROLLER.30, PIC_CONTROLLER.31, R8.P$2, R9.1, R10.1, RESONATOR.GND, SDCARD_CON.P$6, USB_CON.5, X1.3
INT_ACC@RB2: ACCERELOMETER.8, PIC_CONTROLLER.11
L_GND@RA3: LIGHTSENSE.1, PIC_CONTROLLER.22
L_OUT@RA5: LIGHTSENSE.3, PIC_CONTROLLER.24, R7.1
unnamed: PIC_CONTROLLER.33, RESONATOR.1
unnamed: PIC_CONTROLLER.32, RESONATOR.2
unnamed: C2_32KHZ.1, PIC_CONTROLLER.34, SMD_CRYSTAL.P$1
unnamed: C1_32KHZ.1, PIC_CONTROLLER.35, SMD_CRYSTAL.P$2
unnamed: DIOD_OL.A, L_OL.P$2, N_MOS_OL.1
OL_FB: CON_OLED.P5, C_OL_FB.1, R9.2, R12.1
OL_IREF: CON_OLED.P26, R10.2
OL_SENSE: CON_OLED.P6, N_MOS_OL.2, R8.P$3
OL_SW: CON_OLED.P3, N_MOS_OL.3
OL_VBREF: CON_OLED.P7, C_OL_VBREF.1
OL_VCOMH: CON_OLED.P16, C_OL_VCOMH.2
OL_VPP_12V: CON_OLED.P17, C_OL_VPP.+, DIOD_OL.C, R12.2
POK: CHARGER.3, PIC_CONTROLLER.19, R3.1
PROG_CLK@RB6: PIC_CONTROLLER.16, X1.2
PROG_DATA@RB7: PIC_CONTROLLER.17, X1.4
PROG_MCLR@MCLR: PIC_CONTROLLER.18, R1.1, X1.1
PWRGD: LDO.4, PIC_CONTROLLER.20, R5.1
RD_OLED@RE0: CON_OLED.P15, PIC_CONTROLLER.25
RES_OLED: CON_OLED.P12, R11.1
SCLK: ACCERELOMETER.14, PIC_CONTROLLER.36, SDCARD_CON.P$5
SDI: ACCERELOMETER.13, PIC_CONTROLLER.12, SDCARD_CON.P$3
SDO_SPI&D6_OLED@RD6: ACCERELOMETER.12, CON_OLED.P24, PIC_CONTROLLER.4, R2.1, SDCARD_CON.P$7
USB_D+@RC5: PIC_CONTROLLER.43, USB_CON.3
USB_D-@RC4: PIC_CONTROLLER.42, USB_CON.2
VDDCORE: C_UC_VDDCORE.1, PIC_CONTROLLER.23
VUSB: CHARGER.1, C_PWR_VUSB.1, USB_CON.1
V_BAT: BAT.1, CHARGER.5, C_PWR_BAT.1, C_PWR_SW.1, LDO.1, LDO.3
WR_OLED@RE1: CON_OLED.P14, PIC_CONTROLLER.26

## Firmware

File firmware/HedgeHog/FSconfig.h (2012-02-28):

/********************************************************************
 FileName:     	FSconfig.h,     the HedgeHog's SD configuration
 Dependencies:
 Processor:	PIC18F46J50
 Hardware:	Porcupine HedgeHog BASIC, OLED, or TESTBED
 Compiler:  	Microchip C18
 Author:        KristofVL
 ********************************************************************/


#ifndef _FS_DEF_

#include "HardwareProfile.h"

/***************************************************************************/
/*   Note:  There are likely pin definitions present in the header file    */
/*          for your device (SP-SPI.h, CF-PMP.h, etc).  You may wish to    */
/*          specify these as well                                          */
/***************************************************************************/
   
// The FS_MAX_FILES_OPEN #define is only applicable when Dynamic
// memeory allocation is not used (FS_DYNAMIC_MEM not defined).
// Defines how many concurent open files can exist at the same time.
// Takes up static memory. If you do not need to open more than one
// file at the same time, then you should set this to 1 to reduce
// memory usage
#define FS_MAX_FILES_OPEN 	1
/************************************************************************/

// The size of a sector
#define MEDIA_SECTOR_SIZE 		512
/************************************************************************/



/******************************************************************************/
/***Compiler options to enable/Disable Features based on user's application ***/
/******************************************************************************/


// Uncomment this to use the FindFirst, FindNext, and FindPrev
//#define ALLOW_FILESEARCH
/************************************************************************/
// Comment this line out if you don't intend to write data to the card
//#define ALLOW_WRITES
/************************************************************************/
// Comment this line out if you don't intend to format your card
// Writes must be enabled to use the format function
//#define ALLOW_FORMATS
/************************************************************************/
// Uncomment this definition if you're using directories
// Writes must be enabled to use directories
//#define ALLOW_DIRS
/************************************************************************/

// Allows the use of FSfopenpgm, FSremovepgm, etc with PIC18
#if defined(__18CXX)
//    #define ALLOW_PGMFUNCTIONS
#endif
/************************************************************************/

// Allows the use of the FSfprintf function
// Writes must be enabled to use the FSprintf function
//#define ALLOW_FSFPRINTF
/************************************************************************/

// If FAT32 support required then uncomment the following
//#define SUPPORT_FAT32
/* ******************************************************************************************************* */




// Select how you want the timestamps to be updated
// Use the Real-time clock peripheral to set the clock
// You must configure the RTC in your application code
//#define USEREALTIMECLOCK
// The user will update the timing variables manually using the SetClockVars function
// The user should set the clock before they create a file or directory (Create time),
// and before they close a file (last access time, last modified time)
//#define USERDEFINEDCLOCK
// Just increment the time- this will not produce accurate times and dates
#define INCREMENTTIMESTAMP

#ifdef USE_PIC18
	#ifdef USEREALTIMECLOCK
		#error The PIC18 architecture does not have a Real-time clock and calander module
	#endif
#endif

#ifdef ALLOW_PGMFUNCTIONS
	#ifndef USE_PIC18
		#error The pgm functions are unneccessary when not using PIC18
	#endif
#endif

#ifndef USEREALTIMECLOCK
    #ifndef USERDEFINEDCLOCK
        #ifndef INCREMENTTIMESTAMP
            #error Please enable USEREALTIMECLOCK, USERDEFINEDCLOCK, or INCREMENTTIMESTAMP
        #endif
    #endif
#endif

/************************************************************************/
// Define FS_DYNAMIC_MEM to use malloc for allocating
// FILE structure space.  uncomment all three lines
/************************************************************************/
#if 0
	#define FS_DYNAMIC_MEM
	#ifdef USE_PIC18
		#define FS_malloc	SRAMalloc
		#define FS_free		SRAMfree
	#else
		#define FS_malloc	malloc
		#define FS_free		free
	#endif
#endif

// Associate the physical layer functions with the correct physical layer
// USE_SD_INTERFACE_WITH_SPI       // SD-SPI.c and .h

    #define MDD_MediaInitialize     MDD_SDSPI_MediaInitialize
    #define MDD_MediaDetect         MDD_SDSPI_MediaDetect
    #define MDD_SectorRead          MDD_SDSPI_SectorRead
    #define MDD_SectorWrite         MDD_SDSPI_SectorWrite
    #define MDD_InitIO              MDD_SDSPI_InitIO
    #define MDD_ShutdownMedia       MDD_SDSPI_ShutdownMedia
    #define MDD_WriteProtectState   MDD_SDSPI_WriteProtectState
    #define MDD_ReadSectorSize      MDD_SDSPI_ReadSectorSize
    #define MDD_ReadCapacity        MDD_SDSPI_ReadCapacity
    #define MDD_FINAL_SPI_SPEED     2000000


#endif

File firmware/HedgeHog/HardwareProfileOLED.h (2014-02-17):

/********************************************************************
 FileName:     	HardwareProfileOLED.h
 Dependencies:
 Processor:	PIC18F46J50
 Hardware:	Porcupine HedgeHog OLED
 Compiler:  	Microchip C18
 Author:        KristofVL
 ********************************************************************/

#ifndef HARDWARE_PROFILE_HEDGEHOG_OLED_H
#define HARDWARE_PROFILE_HEDGEHOG_OLED_H

/*******************************************************************/
/******** Board-specific definitions *******************************/
/*******************************************************************/
#define CLKFREQ_LOG 8000000
#define CLKFREQ_USB 48000000

extern char is_logging;

// used for some of the time-out counters:
#define GetInstructionClock() ((is_logging)?CLKFREQ_LOG:CLKFREQ_USB)
#define GetSystemClock() (CLKFREQ_USB)

#define DISPLAY_ENABLED		// use the oled display
//#define SOFTSTART_ENABLED		// don't use the softstart circuit
#define ADXL345_ENABLED			// use the ADXL345 accelerometer
//#define BMA150_ENABLED		// don't use BMA150 accelerometer

/*******************************************************************/
/******** USB stack hardware selection options *********************/
/*******************************************************************/
// definitions required by the MCHPFSUSB framework. 
//#define USE_SELF_POWER_SENSE_IO
#define tris_self_power     TRISCbits.TRISC2    // Input
#define self_power          1
//#define USE_USB_BUS_SENSE_IO
#define tris_usb_bus_sense  TRISCbits.TRISC2    // Input
#define USB_BUS_SENSE       1 

/*******************************************************************/
/******** Bootloader-compatible HEX file ***************************/
/*******************************************************************/
//Uncomment this to make the output HEX of this project 
//   to be able to be bootloaded using the HID bootloader
//#define PROGRAMMABLE_WITH_USB_HID_BOOTLOADER		

/*******************************************************************/
/******** SPI interface definitions ********************************/
/*******************************************************************/
#define SPICLOCK            TRISCbits.TRISC2
#define SPIIN               TRISDbits.TRISD6
#define SPIOUT              TRISBbits.TRISB3
#define SPICLOCKLAT         LATCbits.LATC2	// Latch pins SCK/SDI/SDO 
#define SPIINLAT            LATDbits.LATD6
#define SPIOUTLAT           LATBbits.LATB3
#define SPICLOCKPORT        PORTCbits.RC2	// Port pins SCK/SDI/SDO 
#define SPIINPORT           PORTDbits.RD6
#define SPIOUTPORT          PORTBbits.RB3
#define SPICON1             SSP2CON1		// Registers SPI module
#define SPISTAT             SSP2STAT
#define SPIBUF              SSP2BUF
#define SPISTAT_RBF         SSP2STATbits.BF
#define SPICON1bits         SSP2CON1bits
#define SPISTATbits         SSP2STATbits
#define SPI_INTERRUPT_FLAG  PIR3bits.SSP2IF 
#define SPIENABLE           SSP2CON1bits.SSPEN

/*******************************************************************/
/******** MDD File System selection options ************************/
/*******************************************************************/
#define USE_PIC18			// used by FSConfig.h
#define USE_SD_INTERFACE_WITH_SPI
#define TRIS_CARD_DETECT    TRISBbits.TRISB4    // Input
#define CARD_DETECT         PORTBbits.RB4 
#define TRIS_WRITE_DETECT   TRISAbits.TRISA3    // Input
#define SD_CS               PORTCbits.RC6	// Chip Select 
#define SD_CS_TRIS          TRISCbits.TRISC6        
#define SD_CD               0 //PORTBbits.RB4	// Card detect 
#define SD_CD_TRIS          TRISBbits.TRISB4
#define WRITE_DETECT        PORTAbits.RA3	// Write protect 
#define SD_WE               PORTAbits.RA3	
#define SD_WE_TRIS          TRISAbits.TRISA3
#define SPI_INTERRUPT_FLAG_ASM PIR3, 7

/*******************************************************************/
/******** OLED display selection options    ************************/
/*******************************************************************/
#define	oledWR			LATEbits.LATE1
#define	oledWR_TRIS		TRISEbits.TRISE1
#define	oledRD			LATEbits.LATE0
#define	oledRD_TRIS		TRISEbits.TRISE0
#define	oledCS			LATEbits.LATE2
#define	oledCS_TRIS		TRISEbits.TRISE2
#define	oledRESET		LATDbits.LATD1
#define	oledRESET_TRIS	TRISDbits.TRISD1
#define	oledD_C			LATBbits.LATB5
#define	oledD_C_TRIS	TRISBbits.TRISB5
// Definitions for reset pin (from oled.h)
#define RST_TRIS_BIT	TRISDbits.TRISD2
#define RST_LAT_BIT		LATDbits.LATD2

/*******************************************************************/
/******** Accelerometer definitions and options ********************/
/*******************************************************************/
#define ACC_CS           LATCbits.LATC7
#define ACC_CS_TRIS      TRISCbits.TRISC7
#define ACC_INT          PORTBbits.RB2
#define ACC_INT_TRIS     TRISBbits.TRISB2


/*******************************************************************/
/******** USB Power Sense pin definitions and options **************/
/*******************************************************************/
#define USBP_INT_TRIS	TRISBbits.TRISB7
#define USBP_INT		PORTBbits.RB7


/*******************************************************************/
/******** Light Sensor definitions and options *********************/
/*******************************************************************/
#define LIGHTCHANNEL	4
#define LIGHT_PWR		PORTBbits.RB0

/*******************************************************************/
/******** remap pins ***********************************************/
/*******************************************************************/
#define ul_reg() { EECON2 = 0x55;EECON2 = 0xAA;PPSCONbits.IOLOCK = 0;}
#define l_reg()   { EECON2 = 0x55;EECON2 = 0xAA;PPSCONbits.IOLOCK = 1;}
//  RP6  as SDO2 (o/p), RP13 as SCK2 (o/p), RP23 as SDI2 (i/P),
#define remap_pins() {ul_reg(); RPOR6=9;RPOR13=10;RPINR21=23;RPINR1=5; l_reg();}

// make sure all pins are output, except for B7 (USB power) and B5 (acc INT)
#define set_unused_pins_to_output() {TRISD=0; TRISB=0b00000101; }

#endif  //HARDWARE_PROFILE_HEDGEHOG_OLED_H

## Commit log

2012-02-29 added eagle files
    [porcupine4v1_5.brd, porcupine4v1_5.sch]
2012-03-02 extra power saving measures
2012-03-05 fixed device blocking by removing explicit ser.open() command
2012-03-07 clarified pin config before logging
2012-03-15 set default acc config to 4g, 200Hz filter bw
2012-03-22 disabled led pin (possible interference when logging)
2012-03-22 fixed an occasional stuck-in-sleep bug by explicitly checking for interrupt pin while logging
2012-04-12 Reduced current drain
2012-08-28 hardware update eagle cad brd/sch and lib files for version 4v1_7
    [porcupine4v1_7.brd, porcupine4v1_7.sch]
2012-08-28 updated eagle schematics
    [porcupine4v1_7.sch]
2012-09-14 added new hardware profile for new sensor prototype
2012-10-18 * bug fix for new sensor prototype logging problem USB power interrupt / POK pin declaration fixed
2012-12-11 following fixes * PIN output/input settings in HardwareProfileBasicNew.h * removing legacy include of the HardwareProfileBasic.h in main.c * using macro for LATD6 in dsleep_alarm.c * ... -> diff plea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
2013-10-25 fixed inconsistency for HedgeHog eagle files
    [porcupine4v1_7.brd, porcupine4v1_7.sch]
2013-11-04 added porcupine4v1_8 to the repository
    [porcupine4v1_8.brd, porcupine4v1_8.sch]
2013-11-04 porcupine4v1_8: added extension pins
    [porcupine4v1_8.brd, porcupine4v1_8.sch]
2013-11-04 porcupine4v1_8: some wires rewired
    [porcupine4v1_8.brd, porcupine4v1_8.sch]
2013-11-04 4.1.8 added bom & fixing
    [porcupine4v1_8-bom.csv, porcupine4v1_8.brd, porcupine4v1_8.sch]
2013-11-05 porcupine4v1_8: updated extension pins (names), shifted some vias
    [porcupine4v1_8.brd, porcupine4v1_8.sch]
2013-11-05 porcupine4v1_8: BOM-list updated
    [porcupine4v1_8-bom.csv]
2013-11-06 porcupine4v1_8: updated component layout
    [porcupine4v1_8.brd, porcupine4v1_8.sch]
2013-11-11 porcupine5: added OLED version
    [porcupine5v1_2.brd, porcupine5v1_2.sch]
2013-11-13 updated oled schematic
    [porcupine5v1_2.brd, porcupine5v1_2.sch]
2013-11-13 updated oled board
    [porcupine5v1_2.brd]
2013-11-15 OLED version updated
    [porcupine5v1_3.brd, porcupine5v1_3.sch]
2013-11-16 OLED version update wiring
    [porcupine5v1_3.brd, porcupine5v1_3.sch]
2013-11-16 OLED version updated components names and values
    [porcupine5v1_3.brd]
2013-11-16 OLED version updated wiring
    [porcupine5v1_3.brd]
2013-11-16 OLED version: update wiring, added layout docs
    [porcupine5v1_3.brd, porcupine5v1_3.sch]
2013-11-17 added oled bom
    [porcupine5v1_3-bom.csv]
2013-11-17 Update porcupine5v1_3-bom.csv
    minor fix
    [porcupine5v1_3-bom.csv]
2013-11-18 updated BOM list
    [porcupine5v1_3-bom.csv]
2013-11-18 OLED BOM updated
    [porcupine5v1_3-bom.csv, porcupine5v1_3.brd]
2013-11-18 updated OLED version: BOM; board; library
    [porcupine5v1_3-bom.csv, porcupine5v1_3.brd, porcupine5v1_3.sch]
2013-11-18 OLED version: fixed BOM list
    [porcupine5v1_3-bom.csv]
2013-11-19 OLED version: updated BOM list
    [porcupine5v1_3-bom.csv]
2013-11-19 OLED version: replaced non-deliverable devices
    [porcupine5v1_3-bom.csv]
2013-11-20 OLED version: updated BOM list (final)
    [porcupine5v1_3-bom.csv]
2013-11-20 OLED version: BOM list updated (important)
    [porcupine5v1_3-bom.csv]
2013-11-21 OLED version: a) updating coil eagle package b) fixing BOM list (resistors)
    [porcupine5v1_3-bom.csv, porcupine5v1_3.brd, porcupine5v1_3.sch]
2013-11-21 OLED version: improved eagle schematics
    [porcupine5v1_3.brd, porcupine5v1_3.sch]
2013-11-26 added resonators to the HedgeHob eagle library; updated basic and oled versions (new version number)
    [porcupine4v1_9.brd, porcupine4v1_9.sch, porcupine5v1_4.brd, porcupine5v1_4.sch]
2013-11-26 updated hedgehog library and next iteration versions
    [porcupine4v1_9.brd, porcupine4v1_9.sch, porcupine5v1_4.brd, porcupine5v1_4.sch]
2013-12-04 updated schematics adding polarity for coil (oled) and resonator
    [porcupine4v1_9.brd, porcupine4v1_9.sch, porcupine5v1_3.brd, porcupine5v1_3.sch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]
2013-12-12 added import and viz prototypes to the install script
2013-12-16 updated hedgehog library (oled display)
    [porcupine5v1_3.brd, porcupine5v1_3.sch, porcupine5v1_4.brd, porcupine5v1_4.sch]
2013-12-17 added OLED DD-12864WE-4A to hedgehog library; reverted v5.1.2 to original layout
    [porcupine5v1_2.brd, porcupine5v1_2.sch]
2013-12-18 OLED v5.1.3 pin layout update
2013-12-19 added new OLEDdisplay
    [porcupine5v1_4.brd, porcupine5v1_4.sch]
2013-12-19 updated new OLED 5.1.4 version
    [porcupine5v1_4.brd, porcupine5v1_4.sch]
2013-12-20 updated OLED 5.1.4 version: wiring
    [porcupine5v1_4.brd]
2014-01-03 added OLED adapter
    [oled_adapter.brd, oled_adapter.sch]
2014-02-08 retain dmesg code just in case
2014-02-08 lsusb now uses fff0 to detect device
2014-02-11 fixed layout bug in 5.1.3 OLED version schematics
    [porcupine5v1_3.sch]
2014-02-17 OLED 5.1.3 mass storage device detected (at least with 1GB cards)
2014-02-19 OLED eagle schematics updated, OLED firmware code update
    [porcupine5v1_3.sch]
2014-04-13 force 100Hz for PIC sampling
2014-05-21 continious logging working 3905 samples
2014-05-22 patched broken-light-sensor probs
2014-06-17 updated porcupine4v1_9 for better placement of components; removed PWRGD
    [porcupine4v1_9.brd, porcupine4v1_9.sch]
2014-06-17 updated porcupine4v1_8: fixed 12MHZ resonator board footprint
    [porcupine4v1_8.brd, porcupine4v1_8.sch]
2014-06-26 updated basic 4.1.9
    [porcupine4v1_9.brd, porcupine4v1_9.sch]
2014-06-27 eagle design update basic 4.1.9
    [porcupine4v1_9.brd, porcupine4v1_9.sch]
2014-07-15 hardware version 4v1_9 updated, removed c_pwr_sw capacitor
    [porcupine4v1_9.brd, porcupine4v1_9.sch]
2014-07-30 version 4.1.9 pre-order
    [porcupine4v1_9.brd]
2014-07-30 v4.1.9: added farnell order numbers
    [porcupine4v1_9.brd, porcupine4v1_9.sch]
2014-08-04 updated 4v1_9 + BOM
    [porcupine4v1_9-bom.csv, porcupine4v1_9.brd, porcupine4v1_9.sch]
2014-08-07 hardware basic 4.1.9 wire and BOM list update
    [porcupine4v1_9-bom.csv, porcupine4v1_9.brd]
2014-08-07 porcupine4v1_9-bom update: microSD connector in stock
    [porcupine4v1_9-bom.csv]
2014-10-14 fixed sd-write address (32bit); fixed POK pin (RD4);
2014-10-21 added 4v1.10
    [porcupine4v1_10.brd, porcupine4v1_10.sch]
2014-10-21 new board moved to hardware folder, some wiring optimized
    [porcupine4v1_10.brd, porcupine4v1_10.sch]
2014-10-21 v4.1.10 wiring optimized
    [porcupine4v1_10.brd, porcupine4v1_10.sch]

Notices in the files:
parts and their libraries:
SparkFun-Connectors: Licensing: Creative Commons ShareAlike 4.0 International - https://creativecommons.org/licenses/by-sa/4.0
